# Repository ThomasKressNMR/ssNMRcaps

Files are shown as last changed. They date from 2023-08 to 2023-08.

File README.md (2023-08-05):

# ssNMRcaps
3d-printed caps for Bruker rotors, from 1.3 mm to 4 mm, made in Fusion 360

Inspired by
Amerein, C., Banerjee, U., Pang, Z., Lu, W., Pimenta, V., Tan, K.O., 2023. In-house fabrication of 1.3 to 7 mm MAS drive caps using desktop 3D printers. Journal of Magnetic Resonance 348, 107391. https://doi.org/10.1016/j.jmr.2023.107391

## 3D Printing
Caps are printed in a Formlabs 3 3d printer, using coloured resin (Yellow) in 25 µm resolution.



Supports (touchpoint 0.3mm) were placed manually as follows:
 


After printing, caps are washed in a FormWash for 10 minutes, then cured for 60 min at 60ºC.

The rough edges of the supports are sanded down by hands after the caps are detached from their support.

## Specs:
### Spinning
-	4mm caps, tested up to 12.5kHz
-	3.2mm caps, thin wall 2.6mm ID or thick wall 2.2mm ID, tested up to 18kHz
-	2.5mm top and bottom caps, (thick or thin wall), tested up to 25kHz
-	1.3mm, top and bottom, tested up to 50kHz

### Background signal:
-	No background detected for 4 mm caps (<sup>1</sup>H zg, and <sup>13</sup>C CP)
-	As the material is based on polyurethane, the caps might induce 1H, 13C background signal.
-	<sup>1</sup>H zg spectrum of the source material (400 MHz / 9.4 T, 5kHZ MAS):
  1H zg

-	<sup>13</sup>C CP spectrum of the source material (400 MHz / 9.4 T, 5kHZ MAS):
13c CP

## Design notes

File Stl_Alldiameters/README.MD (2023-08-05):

# Fine tuning of cap dimensions
It is possible that different printers give different tolerance. A fine adjusting of the diametere might be required. This folder includes a range of diameters that should fit any rotor.

## Script to generate range of diameters

In fusion 360, go to tools > add-in > script and add-ins. Create new python script with content of Param_stl_generator.py. Edit the parameters in the fil:
- paramNAme: variable being varied
- folder: folder where to save the stl
- file: File name
- start: start dimension (diameter in my files), in mm
- end: end dimension (diameter in my files) in mm
-step: step in mm

Then run script.

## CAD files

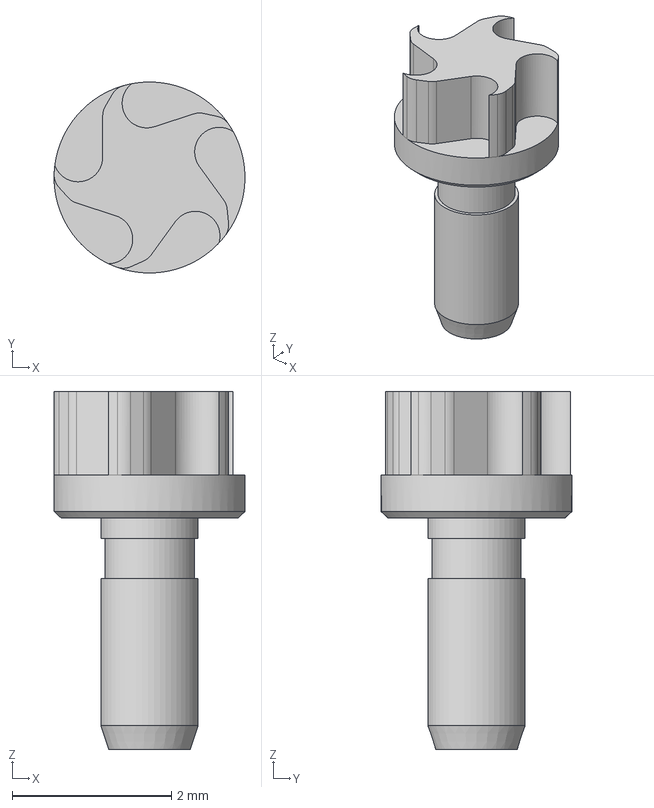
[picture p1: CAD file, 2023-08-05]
STEP/2.5mm/2.5mm_top_thick.step
2.40 x 2.40 x 4.50 mm

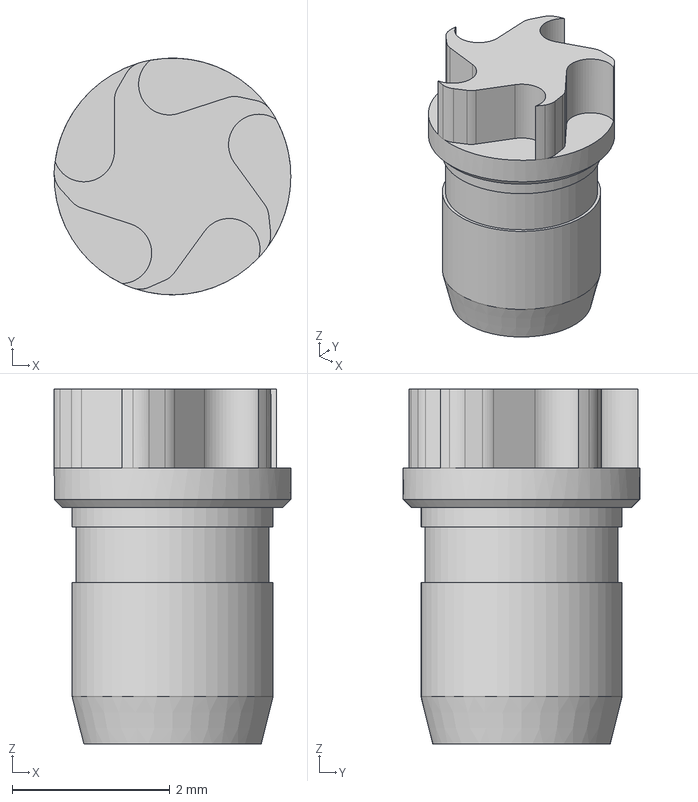
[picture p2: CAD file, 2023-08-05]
STEP/3.2mm/3.2mm.step
3.00 x 3.00 x 4.50 mm

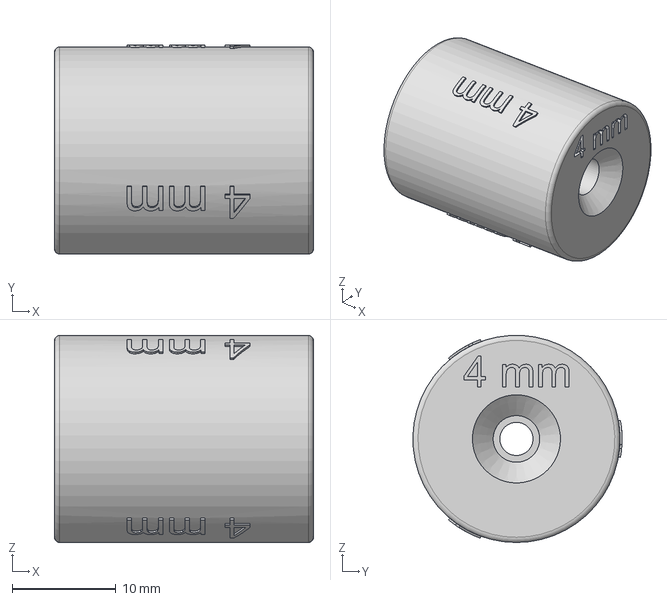
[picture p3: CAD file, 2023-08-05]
STEP/4mm/4mm_funnel.step
25.0 x 20.2 x 20.0 mm

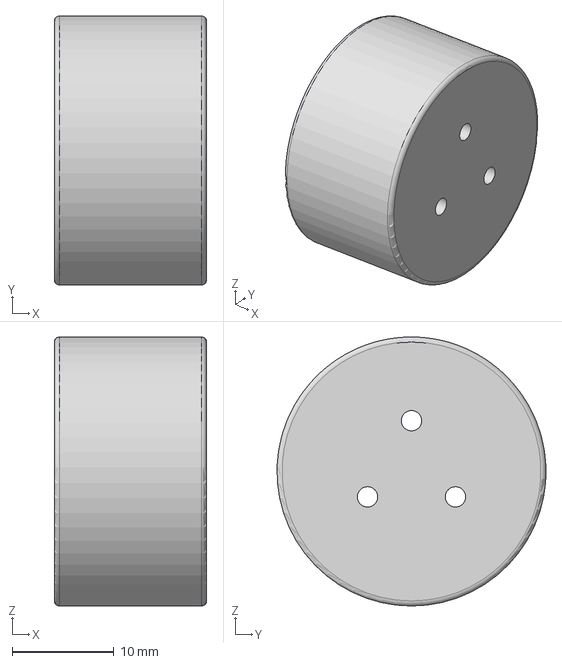
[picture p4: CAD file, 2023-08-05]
STEP/closer.step
15.0 x 26.5 x 26.5 mm

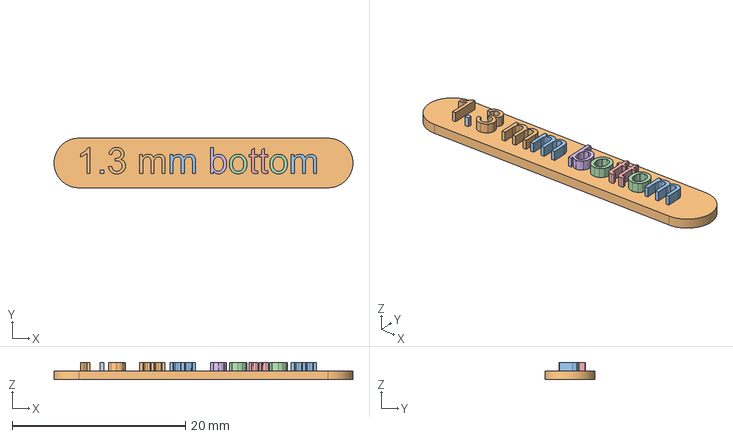
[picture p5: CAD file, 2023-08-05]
STEP/NameTags/1.3mm bottom.step
34.5 x 5.73 x 2.00 mm

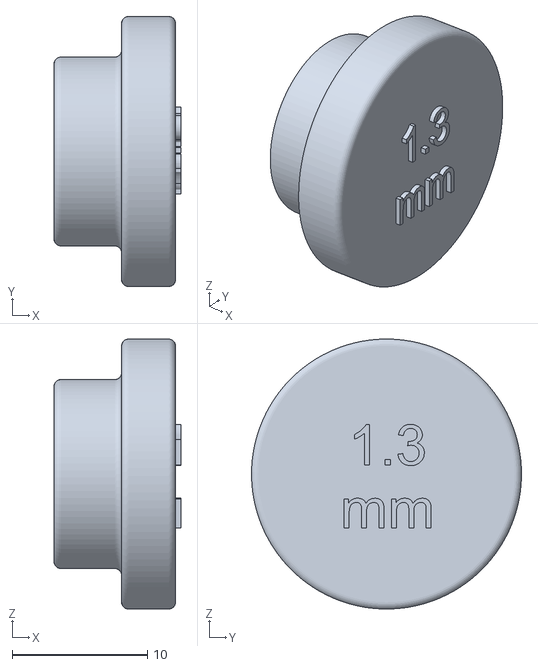
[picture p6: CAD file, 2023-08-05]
stl/1.3mm/1.3mm_closerbottom.stl
9.40 x 20.0 x 20.0

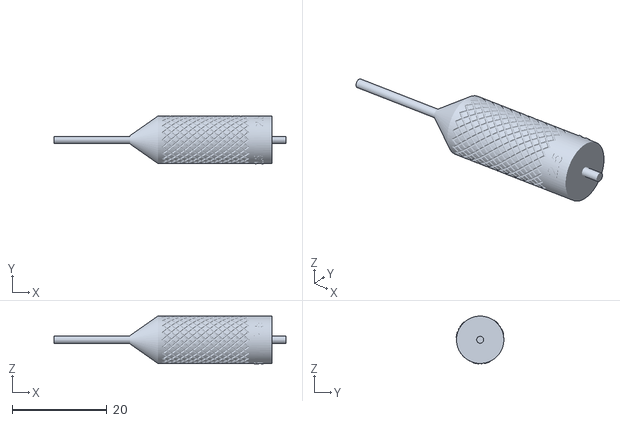
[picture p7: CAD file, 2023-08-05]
stl/2.5mm/2.5mm packing tool.stl
49.0 x 10.1 x 10.1

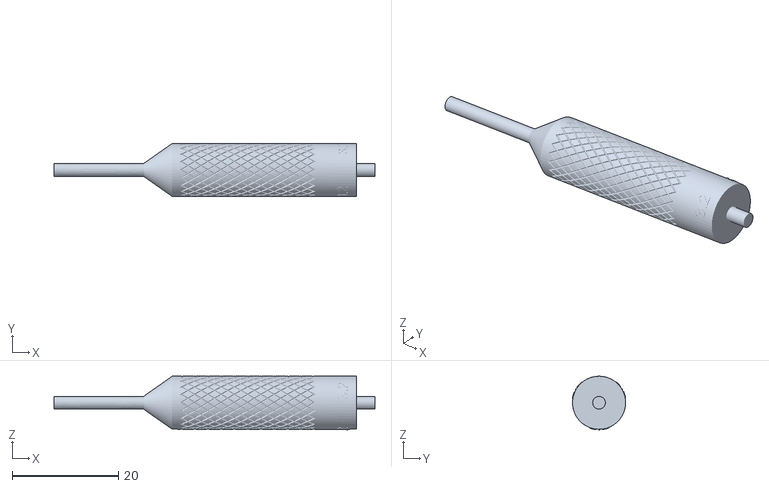
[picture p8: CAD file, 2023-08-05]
stl/3.2mm/3.2mm packing tool.stl
60.5 x 10.1 x 10.1

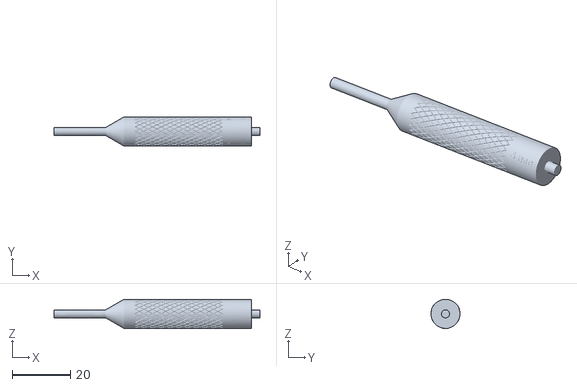
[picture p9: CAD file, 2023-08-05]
stl/4mm/4mm packing tool.stl
71.0 x 10.0 x 10.1

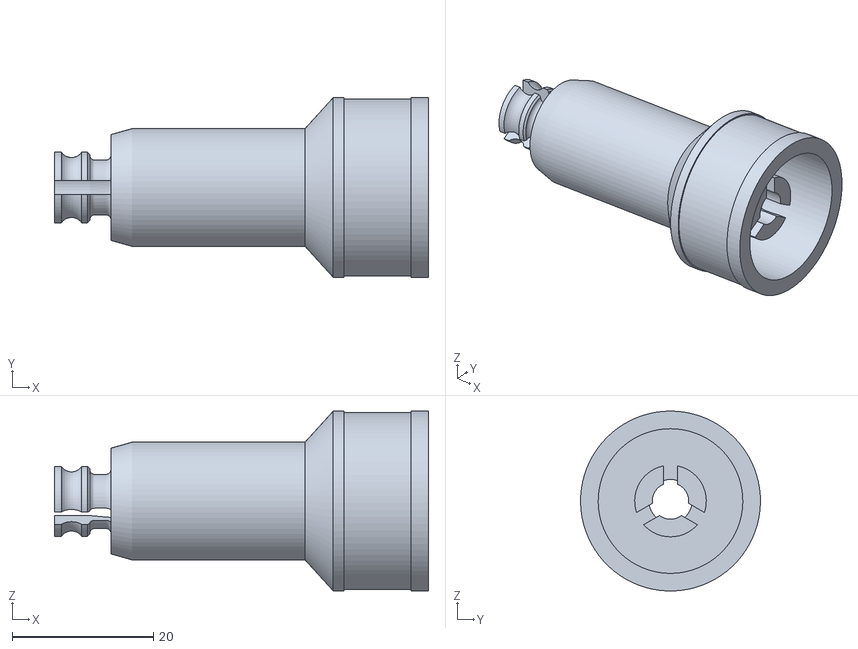
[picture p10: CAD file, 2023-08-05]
stl/SolutionState/spinner.stl
53.0 x 25.5 x 25.5

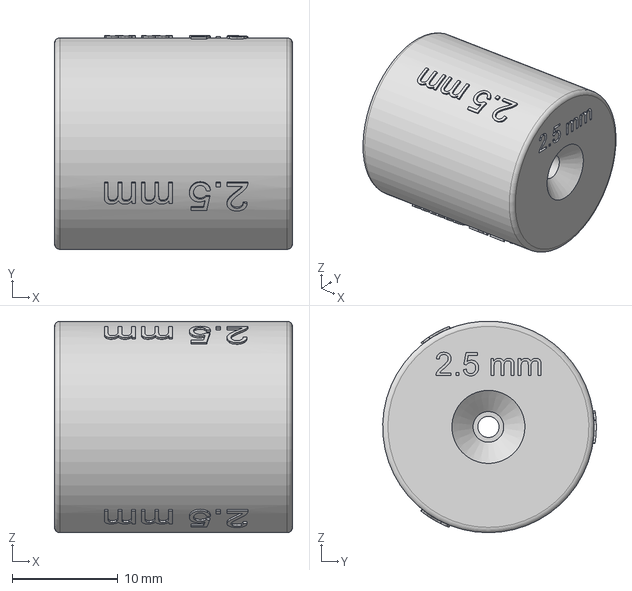
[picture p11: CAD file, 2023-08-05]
STEP/2.5mm/2.5mm_funnel.step
22.5 x 20.2 x 20.0 mm

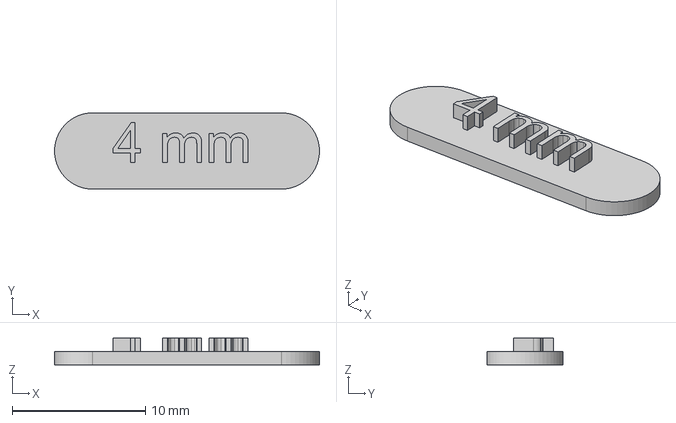
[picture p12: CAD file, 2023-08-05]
STEP/NameTags/4mm.step
19.9 x 5.73 x 2.00 mm

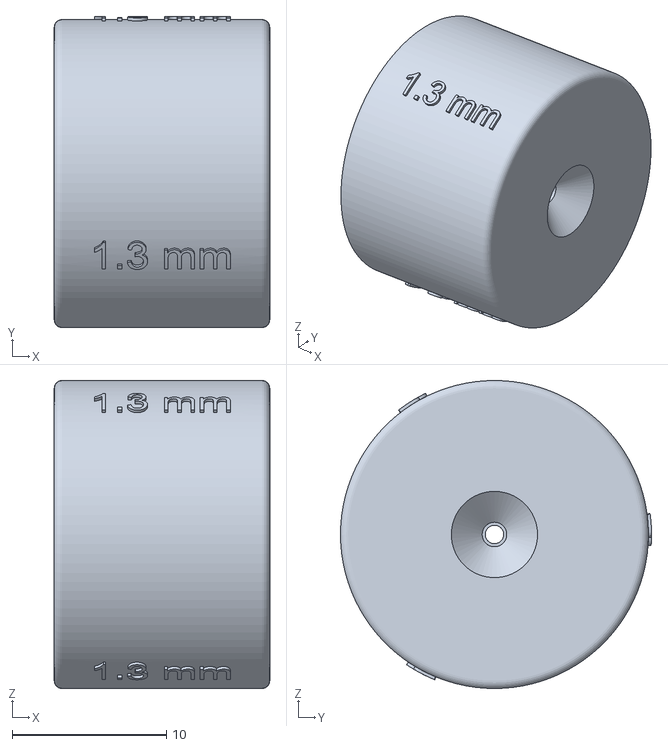
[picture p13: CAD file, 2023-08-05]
stl/1.3mm/1.3mm_funnel.stl
14.0 x 20.2 x 20.0

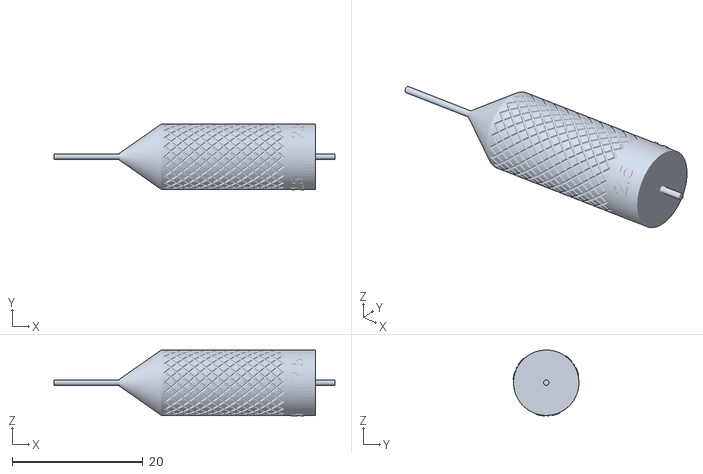
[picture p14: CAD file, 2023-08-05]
stl/2.5mm/2.5mm packing tool_thick.stl
43.0 x 10.1 x 10.1

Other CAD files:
Stl_Alldiameters/3.2mm_2.525.stl
STEP/3.2mm/3.2mm_funnel.step
stl/3.2mm/3.2mm packing tool_thick.stl
stl/4mm/4mm.stl
STEP/2.5mm/2.5mm_bottom.step
STEP/2.5mm/2.5mm_bottom_thick.step
STEP/2.5mm/2.5mm_closing tool.step
STEP/2.5mm/2.5mm_top.step
STEP/3.2mm/3.2mm_closing tool.step
STEP/3.2mm/3.2mm_thickwall.step
STEP/NameTags/1.3mm top.step
STEP/NameTags/2.5mm bottom thick.step
STEP/NameTags/2.5mm bottom thin.step
STEP/NameTags/2.5mm top thick.step
STEP/NameTags/2.5mm top thin.step
STEP/NameTags/3.2mm thick.step
STEP/NameTags/3.2mm thin.step
Stl_Alldiameters/1.3mm_bottom_0.800.stl
Stl_Alldiameters/1.3mm_bottom_0.815.stl
Stl_Alldiameters/1.3mm_bottom_0.830.stl
Stl_Alldiameters/1.3mm_bottom_0.845.stl
Stl_Alldiameters/1.3mm_bottom_0.860.stl
Stl_Alldiameters/1.3mm_bottom_0.875.stl
Stl_Alldiameters/1.3mm_bottom_0.890.stl
Stl_Alldiameters/1.3mm_bottom_0.905.stl
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
